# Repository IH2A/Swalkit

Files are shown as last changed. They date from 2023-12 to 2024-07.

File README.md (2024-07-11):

https://user-images.githubusercontent.com/100538879/157646195-c86fd216-0dd4-412f-9931-ac7addbbb123.mp4

> **Responsabilité  
Toute la documentation est fournie "en l'état", la chaire IH2A ne fournit aucune garantie de quelque élément que ce soit, qu'il soit explicite, implicite ou statutaire, y compris, mais sans s'y limiter, toute garantie de qualité marchande ou l’adéquation à un usage particulier ou toute garantie que le contenu des articles sera sans erreur. La chaire IH2A ne peut en aucun cas engager sa responsabilité pour tout dommage direct ou indirect, ou dommages découlant de l’utilisation de la documentation des projets partagés sur cette plateforme.**

> **Avertissement  
Les objets/projets présentés sur cette plateforme le sont UNIQUEMENT ET EXCLUSIVEMENT à titre d'informations, d'enseignements et d'exploration des possibilités du prototypage réalisable en fablab. Leur mise en avant ne constitue en aucun cas un conseil de professionnel quant à leur usage, elle ne remplace pas l'avis d'un spécialiste médical ou paramédical seul en mesure d'évaluer, de conseiller et de proposer des matériels, imprimés ou non, correspondant à une situation et des besoins précis et personnels faisant suite à la réalisation d'un bilan complet.**

> **Le Github de la chaire IH2A ([https://github.com/IH2A/](https://github.com/IH2A/)) ainsi que toutes les autres plateformes associées à la documentation de nos projets (site de communication de la chaire IH2A, [https://ih2a.insa-rennes.fr/](https://ih2a.insa-rennes.fr/)) sont le reflet de travaux de recherche appliqués aux aides technologiques au sein d'une chaire académique de recherche et de l'intérêt professionnel pour les possibilités offertes par le prototypage collaboratif en fablab.**

> **La situation de handicap est délicate et complexe et doit être évaluée et accompagnée par des professionnels.**

> **Sauf mention contraire, tous les contenus de ce projet sont sous licence [EUPL 1.2](https://eupl.eu/1.2/fr/).**
-----------------------------------------------------------------------------------------------------------------

# 1. Table des matières
- [1. Table des matières](#1-table-des-matières)
- [2. Swalkit : "Smart Walker Kit"](#2-swalkit--smart-walker-kit)
- [3. Étapes de fabrication du Swalkit](#3-étapes-de-fabrication-du-swalkit)
  - [3.1. Les outils](#31-les-outils)
  - [3.2. Le matériel](#32-le-matériel)
  - [3.3. Vue d'ensemble](#33-vue-densemble)
  - [3.4. Notice de montage](#34-notice-de-montage)
  - [3.5. Mode d'emploi du M5 stack](#35-mode-demploi-du-m5-stack)
  - [3.6. Application Android](#36-application-android)
- [4. FAQ](#4-faq)
- [5. Publications](#5-publications)
- [6. Crédits](#6-crédits)

# 2. Swalkit : "Smart Walker Kit"

Le "Swalkit" est un kit open source de "déambulateur intelligent". Il a été développé dans le cadre des travaux de recherche sur l'aide à la navigation par retour haptique pour les personnes utilisatrices de déambulateur ayant des déficiences visuelles, au sein de la [chaire académique IH2A](https://ih2a.insa-rennes.fr/) (Innovations, Handicap, Autonomie et Accessibilité) portée par l'INSA Rennes. Le dispositif "Swalkit" est reproductible : ce dépôt vise à fournir toutes les informations nécessaires afin de pouvoir explorer les possibilités du prototypage réalisables en fablab.

Le kit "Swalkit" est en effet :
- reproductible et adaptable sur des aides techniques existantes ;
- intuitif et facile à prendre en main ;
- personnalisable ; 
- à faible coût.

Le fonctionnement du kit repose sur le retour haptique fourni par les poignées du déambulateur qui informe l'usager de la position des obstacles lors de la déambulation. 
Il est composé de 3 ensembles à fixer sur l'aide technique à équiper : 
- capteurs ;
- moteurs vibrants ;
- unité de contrôle. 

Les capteurs mesurent des distances jusqu'à 80cm. Ils sont positionnés à l'avant du déambulateur, dans des boîtiers imprimés en 3D disposés de chaque côté, afin de permettre la détection d'obstacles devant le déambulateur et sur les côtés. Les moteurs vibrants sont positionnés au plus proches des poignées dans des boîtiers imprimés en 3D. L'unité de contrôle récupère les mesures de distances effectuées par les capteurs puis envoie un signal à chaque moteur pour les activer afin de signaler la présence d'un obstacle à l'usager par vibration de la poignée dans sa main.
<p align="center">walker

Une app mobile Android permet de personnaliser la configuration du comportement des moteurs. Ainsi, il est possible de définir plusieurs profils pour différents usagers et différents contexte d'usage (exemple : intérieur, extérieur, domicile, etc.).
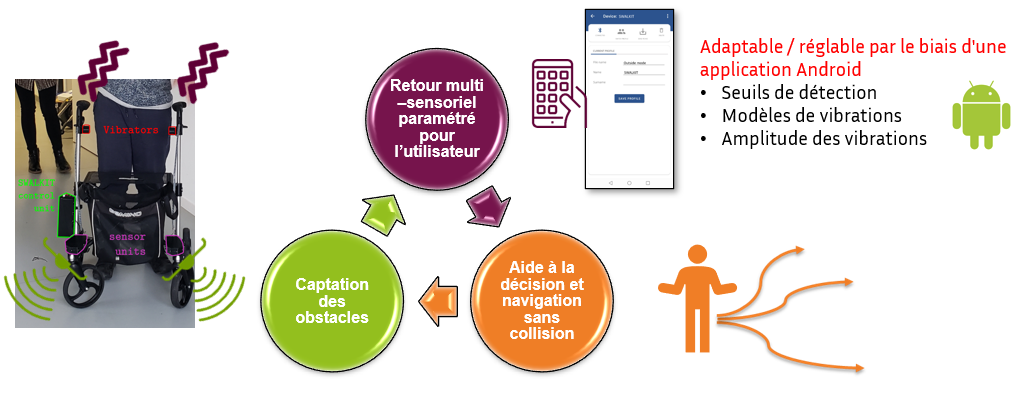
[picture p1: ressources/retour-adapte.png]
schema
<p align="center">

Le reste de la page indique comment fabriquer son kit, et les publications scientifiques dont le kit a fait l'objet.
L'ensemble des sources est disponible sur ce dépot.

> **Attention  
> La chaire IH2A ne fabrique pas de kit et ne fournit pas de kit. Seules les indications de montage et d'assemblage, ainsi qu'une liste de composants, sont indiquées dans ce dépôt.**

# 3. Étapes de fabrication du Swalkit

## 3.1. Les outils

La table suivante indique la liste des outils permettant la fabrication d'un kit :

|   Quel outil ?   |     Pour quoi faire ?                                               |    Remarques   |
|-----------|-|-|
|   Un ordinateur sous Windows    |  Téléverser le programme dans le microcontrôleur M5Stack AtomS3   |  Utiliser l'outil de téléversement fourni (cf [tutoriel](#33-vue-densemble))                                   |
|                   |    Adapter les modèles 3D                                           |  Utliliser un logiciel de modelisation 3d (Fusion360, Solidworks...)    |
|   Une imprimante 3D    |   Imprimer les boîtiers et interfaces mécaniques               |  Une imprimante petit format fera l'affaire         |
|   Un fer à souder    |   Il y a des points de soudure à faire sur une carte PCB pour assigner des adresses différentes aux bus I2C intelligents  |           |
|    |   Il faut souder des câbles sur les moteurs  |           |
|   Un petit tournevis cruciforme |   Pour ouvrir et fermer les différents boîtiers et fixer les capteurs |           |

## 3.2. Le matériel

La table suivante indique la liste du matériel à commander, nécessaire à la fabrication d'un kit :

|   Nom     |    Nom exact |  Pour quoi faire?   |    Fournisseur    |   Quantité nécéssaire    |     Aperçu     | Prix unitraire indicatif |
|-|-|-|-|-|-|-|
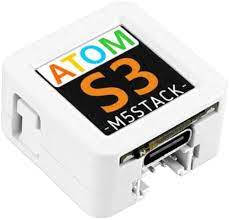
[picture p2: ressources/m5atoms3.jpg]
AtomS3
|AtomS3|M5Stack AtomS3| C'est le microcontrôleur central qui gère les capteurs, les moteurs, la logique, la communication Bluetooth...|[shop.m5stack](https://shop.m5stack.com/products/atoms3-dev-kit-w-0-85-inch-screen); [gotronic](https://www.gotronic.fr/art-module-atoms3-dev-kit-c123-37089.htm)|1|  | 17,40€|
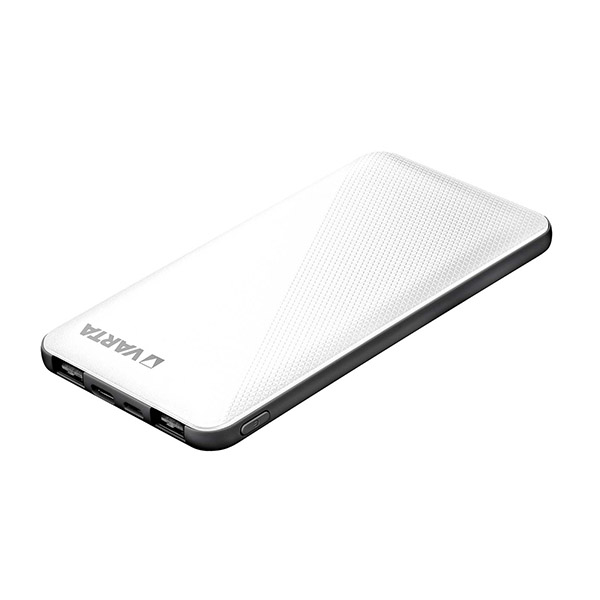
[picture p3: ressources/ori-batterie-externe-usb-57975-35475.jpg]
Batterie
|Batterie|Varta Power bank energy type 57975|C'est l'alimentation de tout le système|[gotronic](https://www.gotronic.fr/art-batterie-externe-usb-57975-35475.htm)|1| |19,90€|
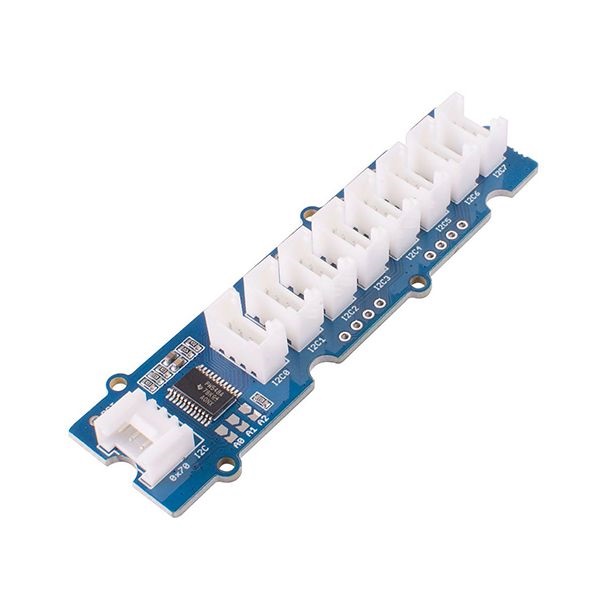
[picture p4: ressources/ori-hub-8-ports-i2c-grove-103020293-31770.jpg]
Smart Hub
|Smart Hub I2C|Grove - 8 Channel I2C Hub (TCA9548A)| Ces hubs gèrent les capteurs et permettent de les différencier sur le bus I2C|[gotronic](https://www.gotronic.fr/art-hub-8-ports-I2C-grove-103020293-31770.htm)|2| |8,05€|
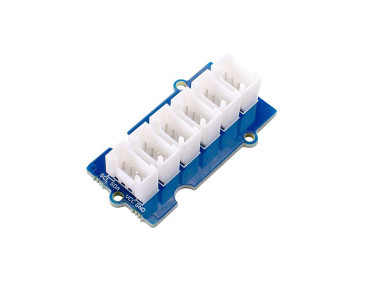
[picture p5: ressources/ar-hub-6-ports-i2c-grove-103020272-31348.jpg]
Hub I2C simple
|Hub I2C simple|Grove - I2C Hub (6 ports) v1.0|Ce hub permet de connecter l'ensemble des dispositifs sur le même bus I2C|[gotronic](https://www.gotronic.fr/art-hub-6-ports-I2C-grove-103020272-31348.htm)|1| |1,90€|
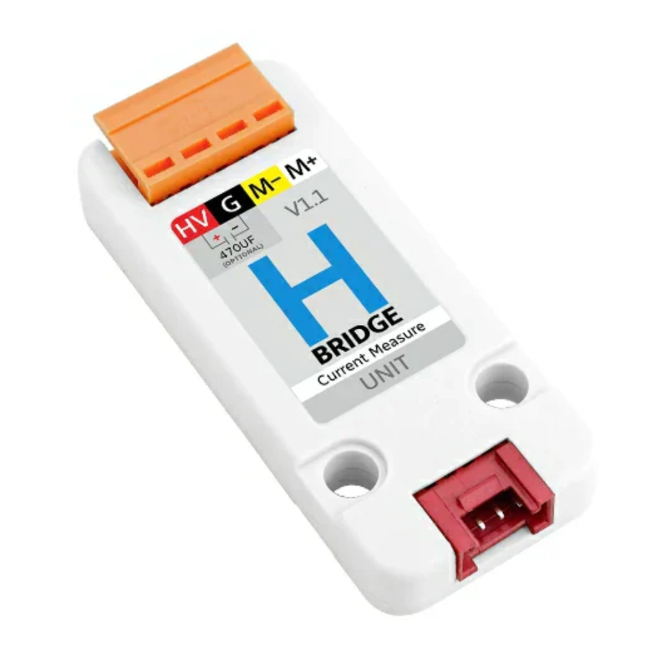
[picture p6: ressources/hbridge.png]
Pont en H
|Pont en H|Hbridge v1.1 Unit (stm32F030)|C'est un circuit électronique utilisé pour contrôler l'intensité du courant traversant un moteur|[shop.m5stack](https://shop.m5stack.com/products/h-bridge-unit-v1-1-stm32f030)|2||9€|
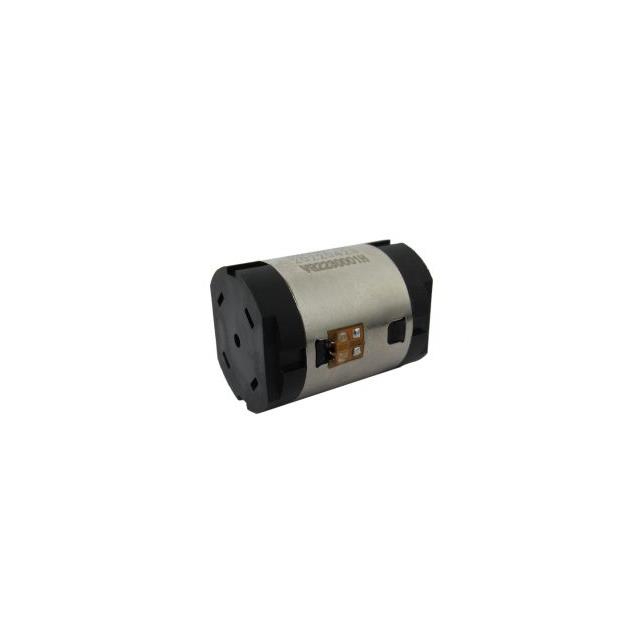
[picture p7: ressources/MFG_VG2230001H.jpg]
Moteur LMA
|Moteur LMA| - |Ce sont les moteur vibrants à positionner près des poignées du déambulateur|[digikey](https://www.digikey.fr/en/products/detail/vybronics-inc/VG2230001H/16719289)|2||7,09€|
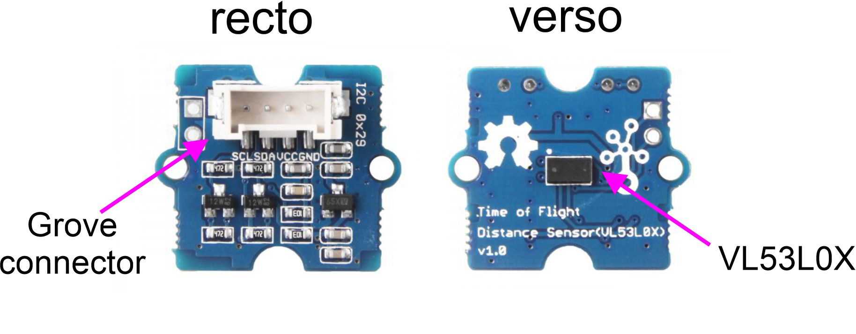
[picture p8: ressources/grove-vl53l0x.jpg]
Capteurs
|Capteurs TOF| Grove - Time of Flight Distance Sensor (VL53L0X) | Capteur "Time of flight" VL53L0X permettant la détection d'un objet dans une plage de 3 à 100 cm|[gotronic](https://www.gotronic.fr/art-module-grove-time-of-flight-101020532-28252.htm#complte_desc)|8||15,65€|
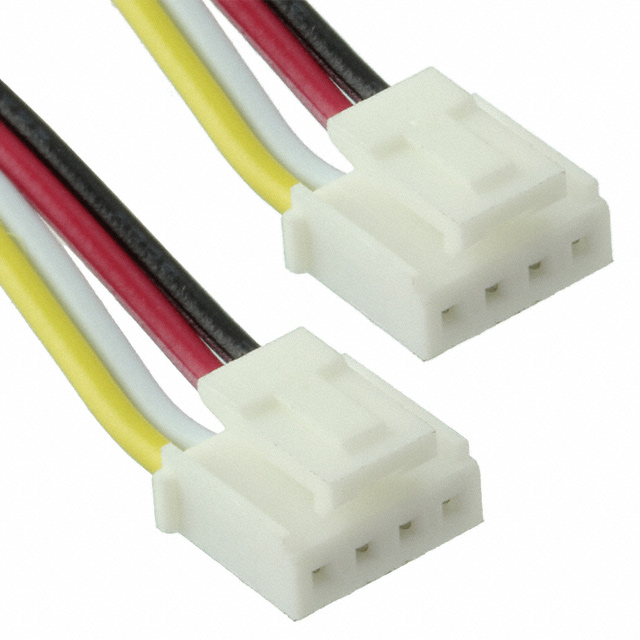
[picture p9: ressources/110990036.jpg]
grove court
|Câble grove 5cm| - |Câbles courts pour connecter les composants sur le bus I2C|[digikey](https://www.digikey.fr/en/products/detail/seeed-technology-co-ltd/110990036/5482563)|3 lots de 5||1,91€|
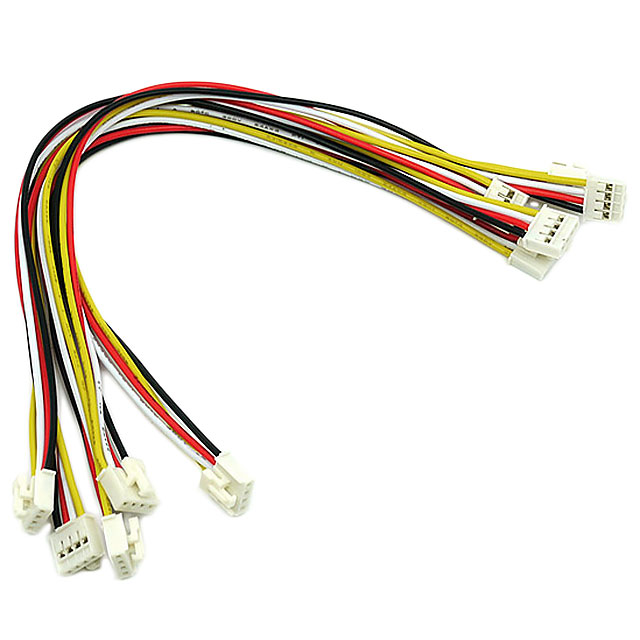
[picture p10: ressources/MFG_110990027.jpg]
grove long
|Câble grove 30cm| - |Câbles longs pour connecter les composants sur le bus I2C|[digikey](https://www.digikey.fr/en/products/detail/seeed-technology-co-ltd/110990040/5482564)|1 lot de 5||2,92€|
|Câble grove 100cm| - |Câbles très longs pour connecter les composants sur le bus I2C|[mouser](https://www.mouser.fr/ProductDetail/M5Stack/A034-D?qs=81r%252BiQLm7BQIX3ZPS9TpAA%3D%3D)|1 lot de 5|grove long|1,81€|
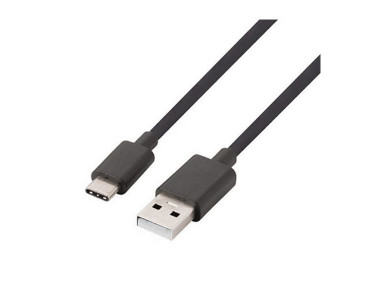
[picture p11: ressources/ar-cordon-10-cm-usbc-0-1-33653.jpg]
USBC
|Câble USB-C| - |Pour téléverser le programme, alimenter l'atomS3 et recharger la batterie|[gotronic](https://www.gotronic.fr/art-cordon-10-cm-usbc-0-1-33653.htm)|1||4,30€|
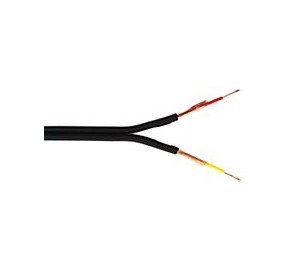
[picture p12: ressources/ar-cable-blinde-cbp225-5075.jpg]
câble
|Câble d'alimentation moteur| - |Pour alimenter les moteurs vibrants|à titre indicatif: [gotronic](https://www.gotronic.fr/art-câble-blinde-cbp225-5075.htm)|2 mètres||~1€/m|
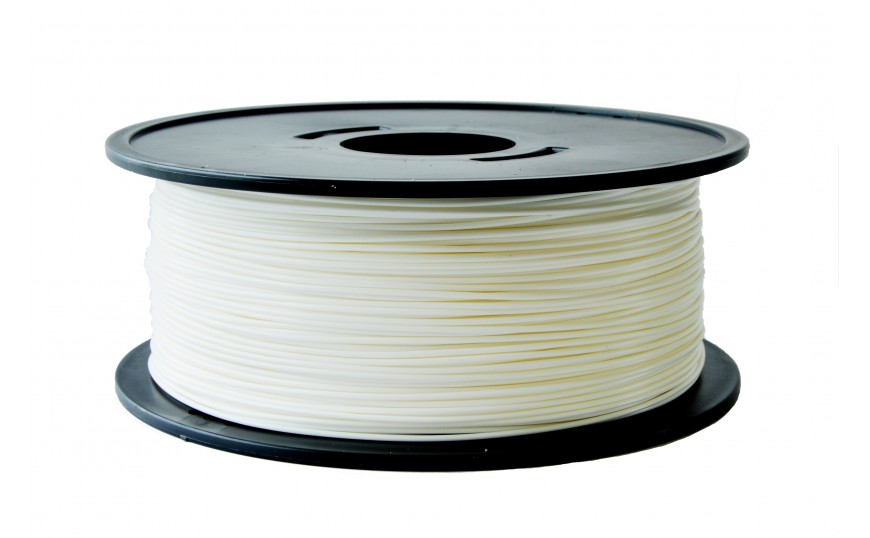
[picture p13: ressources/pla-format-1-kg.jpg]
PLA
|Bobine PLA| - |Pour imprimer les boîtiers|à titre indicatif : [arianeplast](https://www.arianeplast.com/3d-filament-recycle/195-pla-recycle-couleur-metallise-filament-175mm.html)|<1kg||~20€/kg|
|Visserie| - |Pour l'assemblage|[M3x8mm = 6</br>M3x15mm = 14</br>Écrous M3 = 20</br>M2x8mm = 25</br>Écrous M2 = 16](https://www.bricovis.fr/produit-vis-a-tete-fraisee-hexagonale-creuse-filetage-total-inox-a2-din-7991-tfhca2/)|-||
|Gaine spirale| - |Pour organiser les câbles|[leroy merlin](https://www.leroymerlin.fr/produits/electricite-domotique/rallonge-multiprise-enrouleur-et-cable-electrique/gaine-electrique-icta/gaine-spirale-p.html)|2 mètres||
|Scotch| - |Pour coller les moteurs||-||
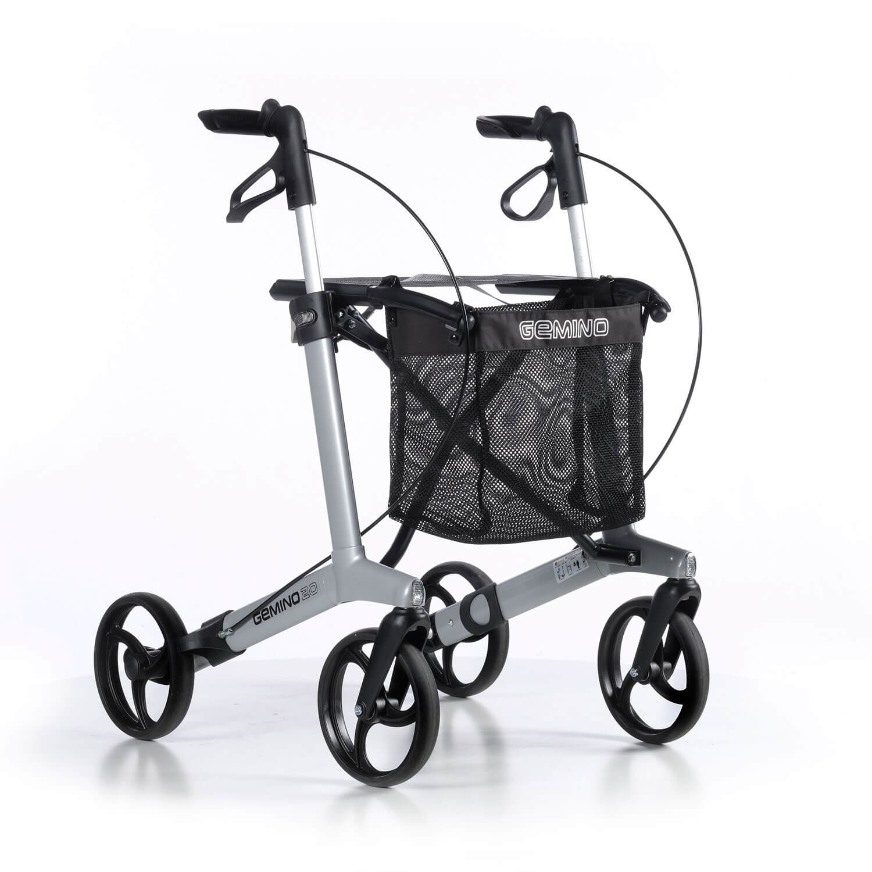
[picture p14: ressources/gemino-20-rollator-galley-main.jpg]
rollator
|Déambulateur| - |Le gemino est utilisé comme base||1||615€|

## 3.3. Vue d'ensemble

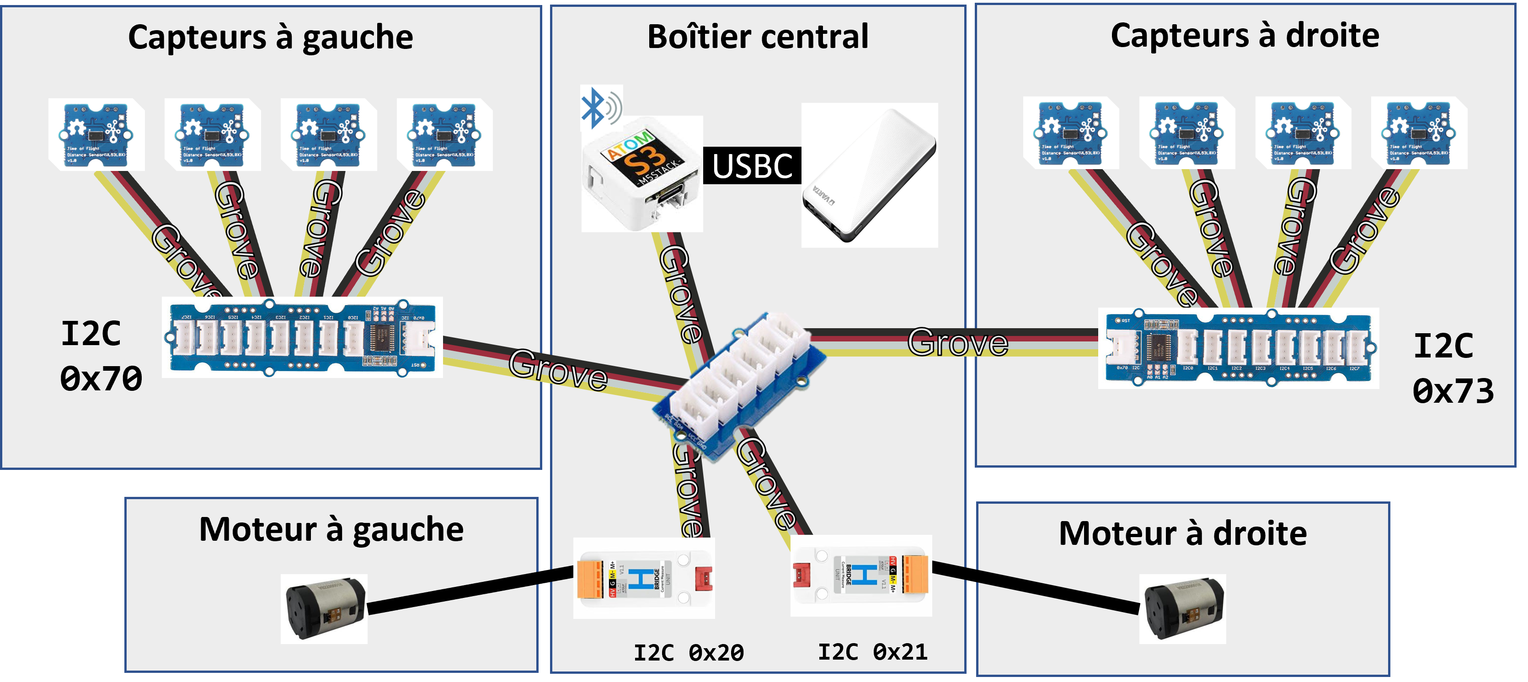
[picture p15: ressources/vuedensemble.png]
vuedensemble


## 3.4. Notice de montage

> Note de première mise en route : Lorsque le programme est téléversé le M5stack démarre. Celui-ci commence à communiquer avec les différents modules. Les ponts en H ont besoin d'être mis à jour pour contrôler correctement les moteurs. En effet, ces moteurs ont besoin d'une alimentation qui alterne son sens à 70Hz pour fonctionner correctement. Or, le programme de ces ponts en H alterne le sens du courant à la demande. **Nous mettons à jour ce programme automatiquement via le M5Stack et la communication I2C** pour que l'alternance de sens soit gérée directement dans le pont en H.

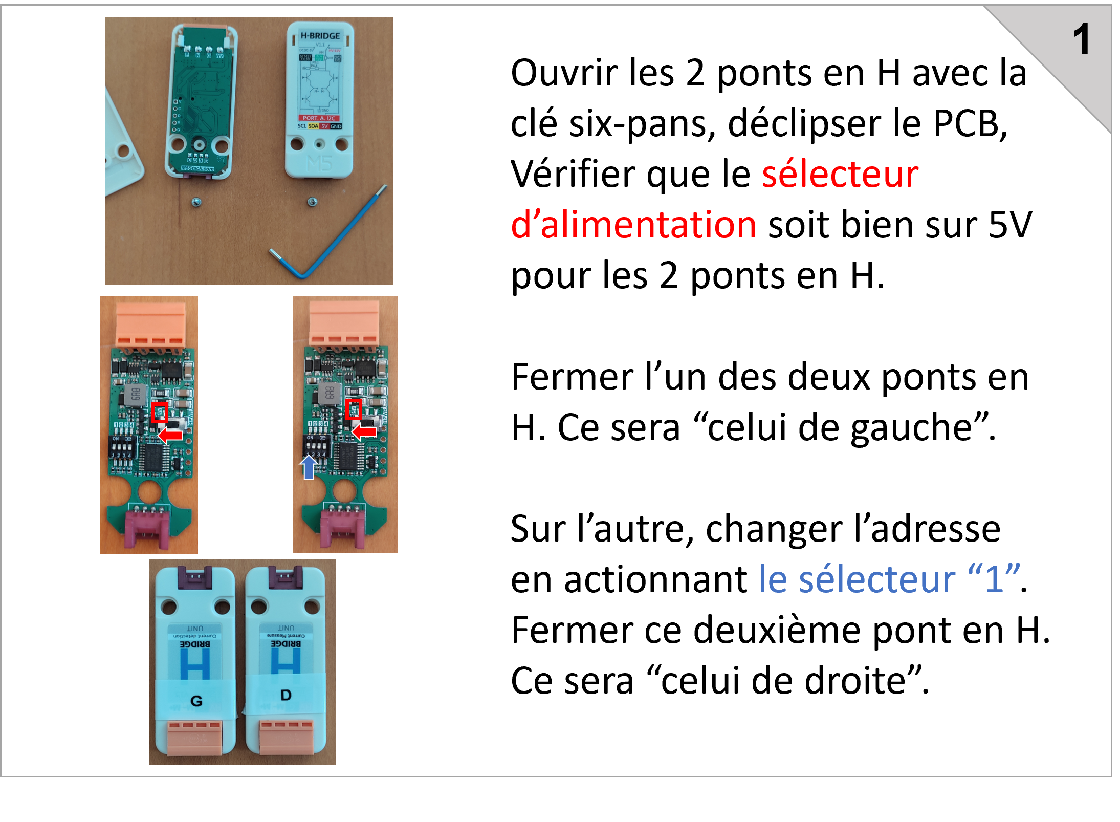
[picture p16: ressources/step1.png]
step1

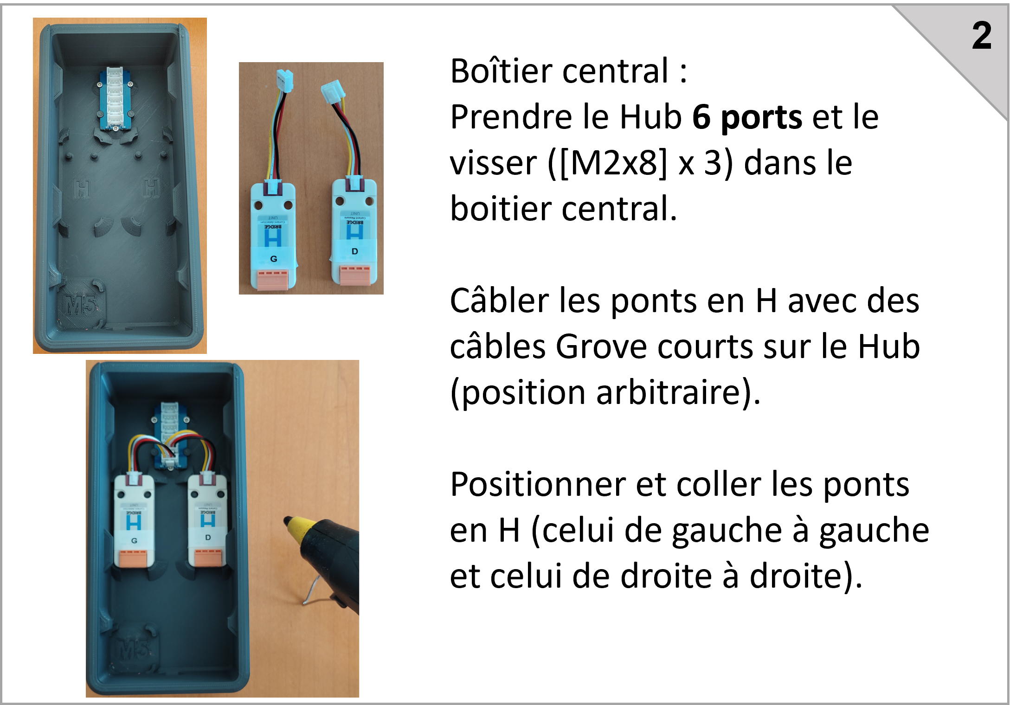
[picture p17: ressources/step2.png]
step2

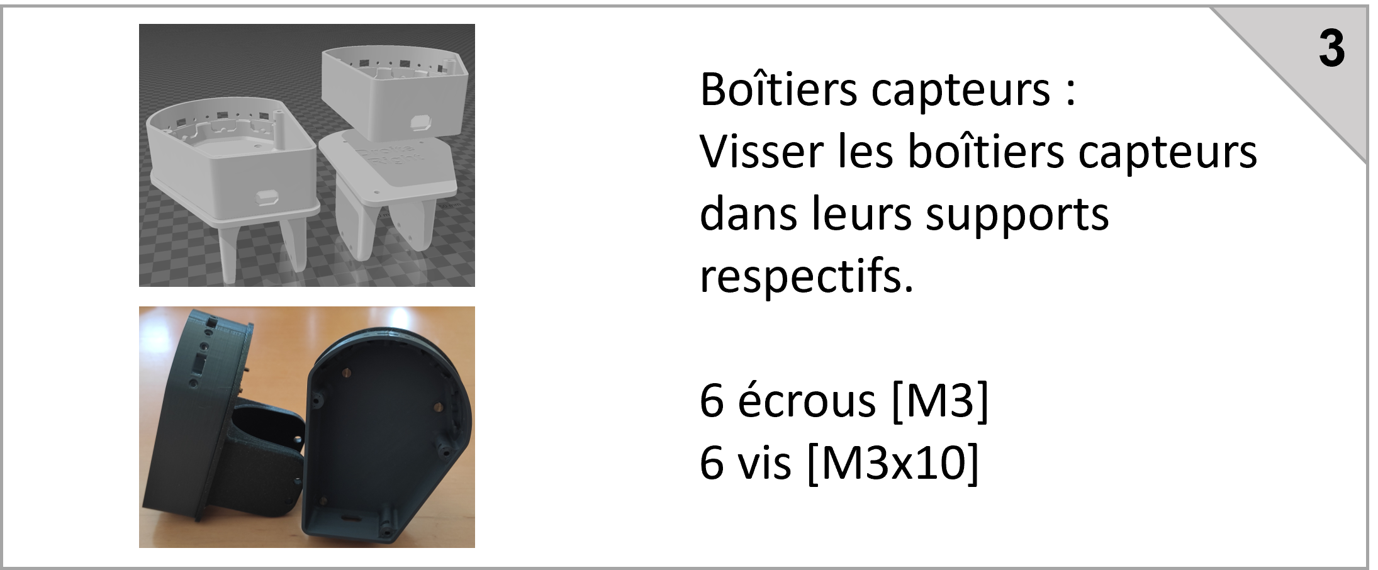
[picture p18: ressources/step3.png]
step3

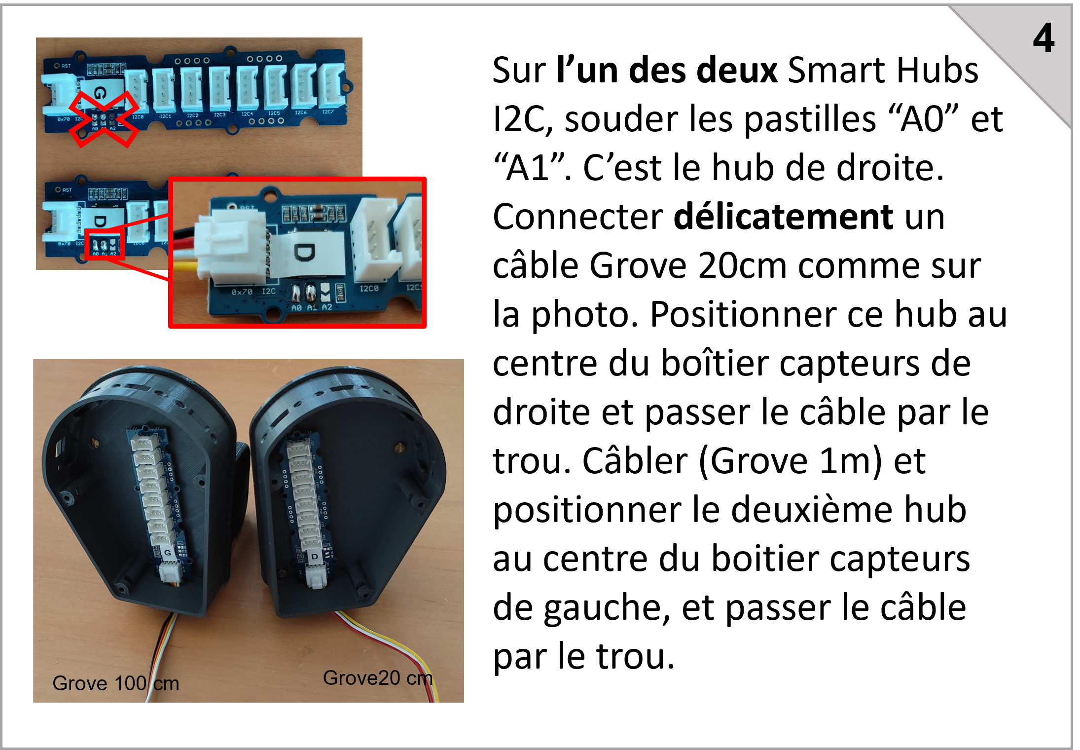
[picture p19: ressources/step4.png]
step4

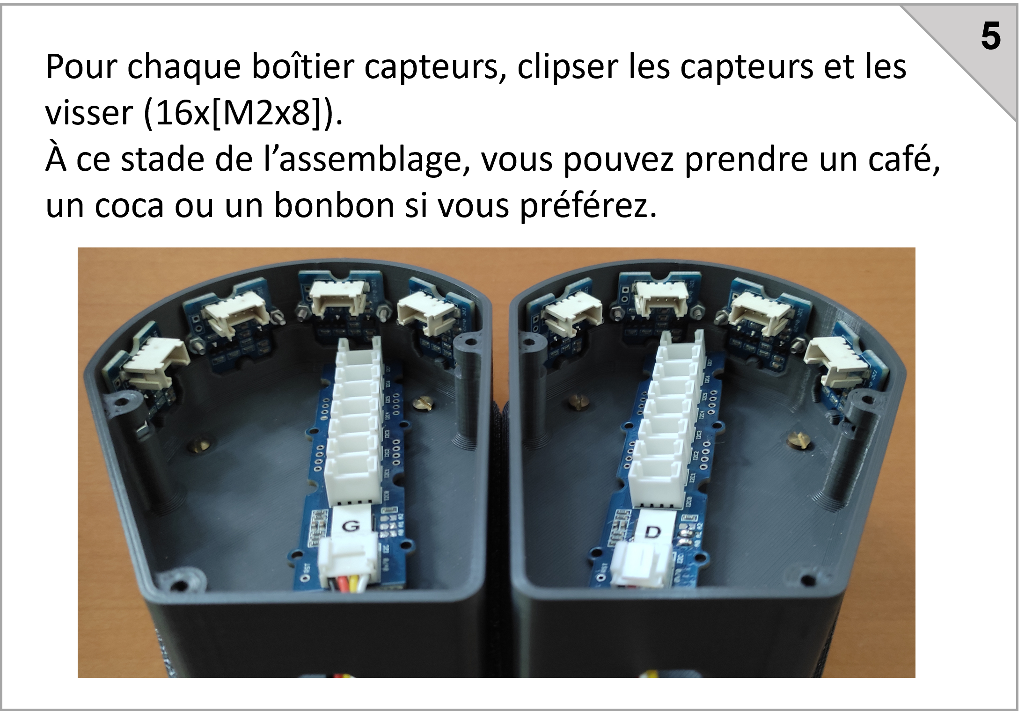
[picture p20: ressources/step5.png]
step5

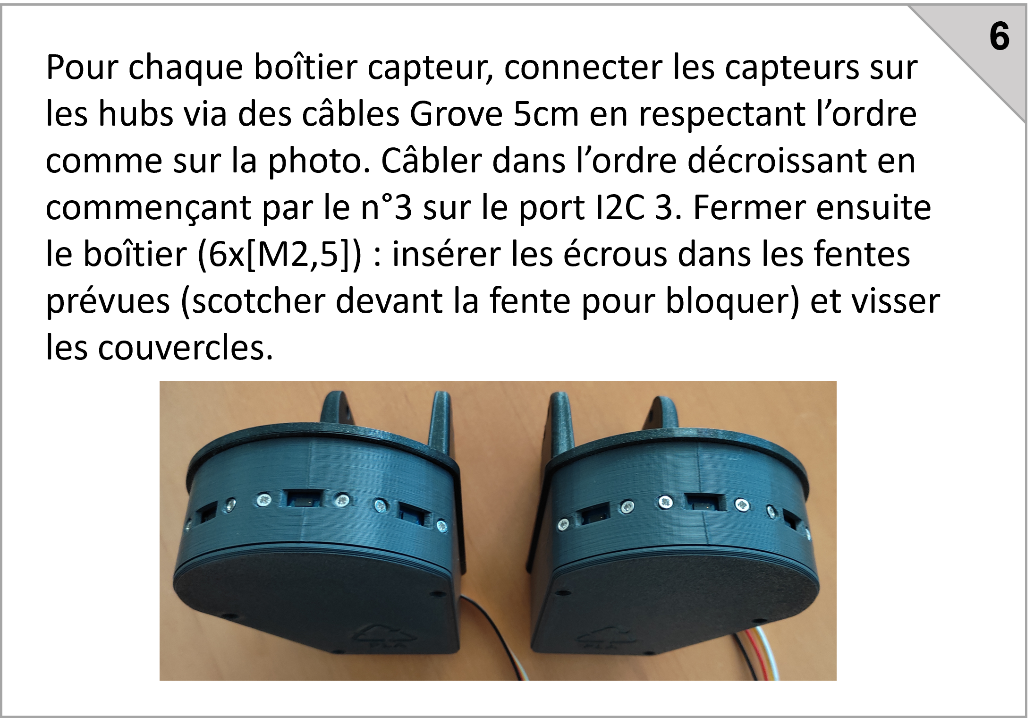
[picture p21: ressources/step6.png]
step6

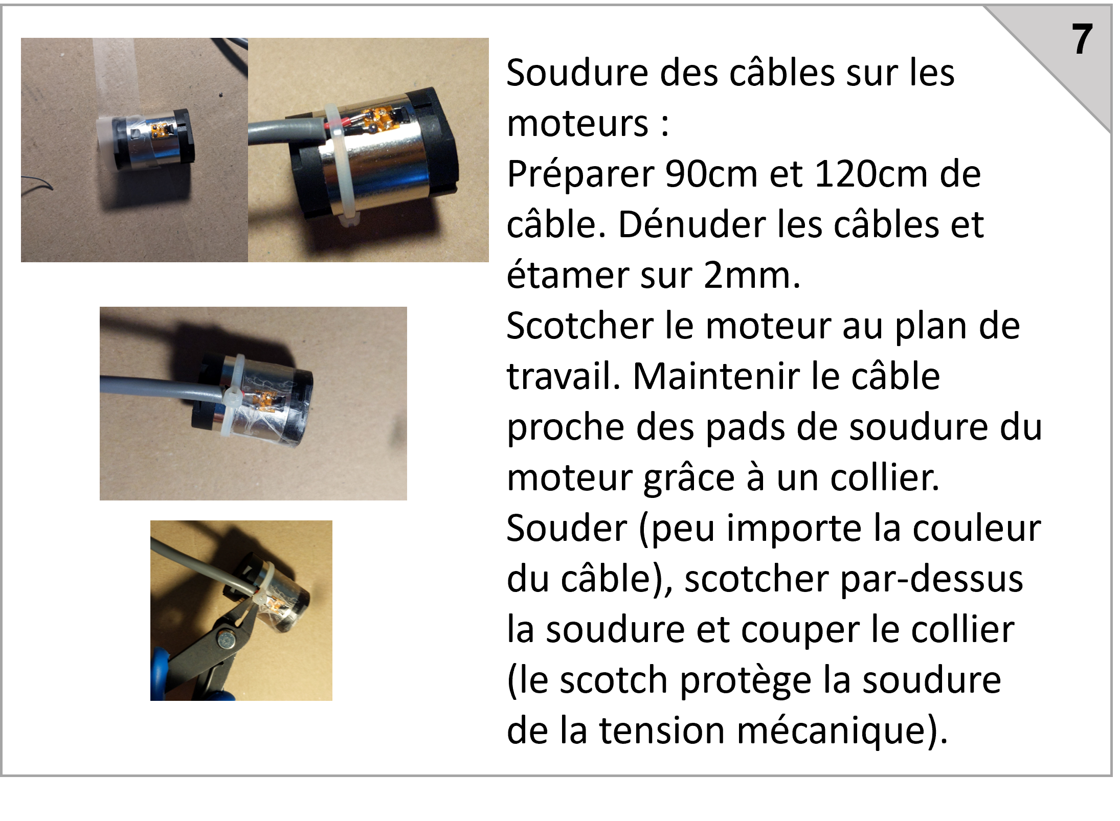
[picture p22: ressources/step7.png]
step7

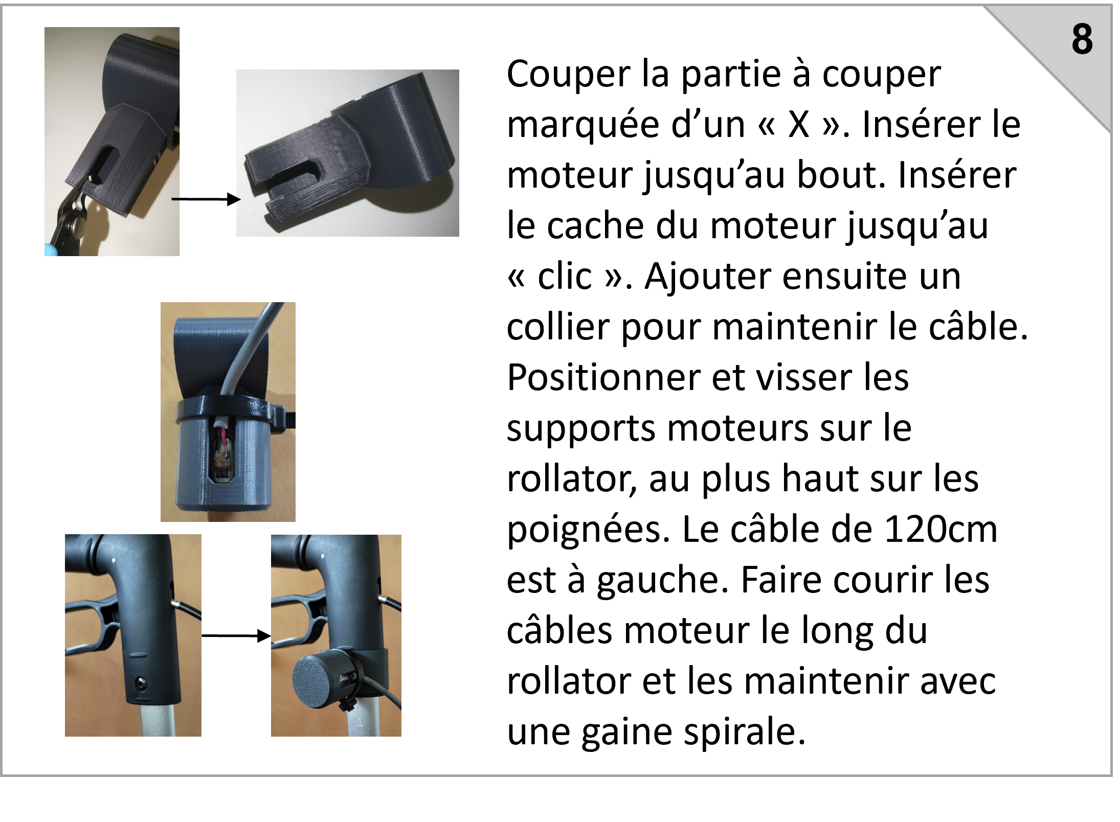
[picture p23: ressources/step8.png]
step8

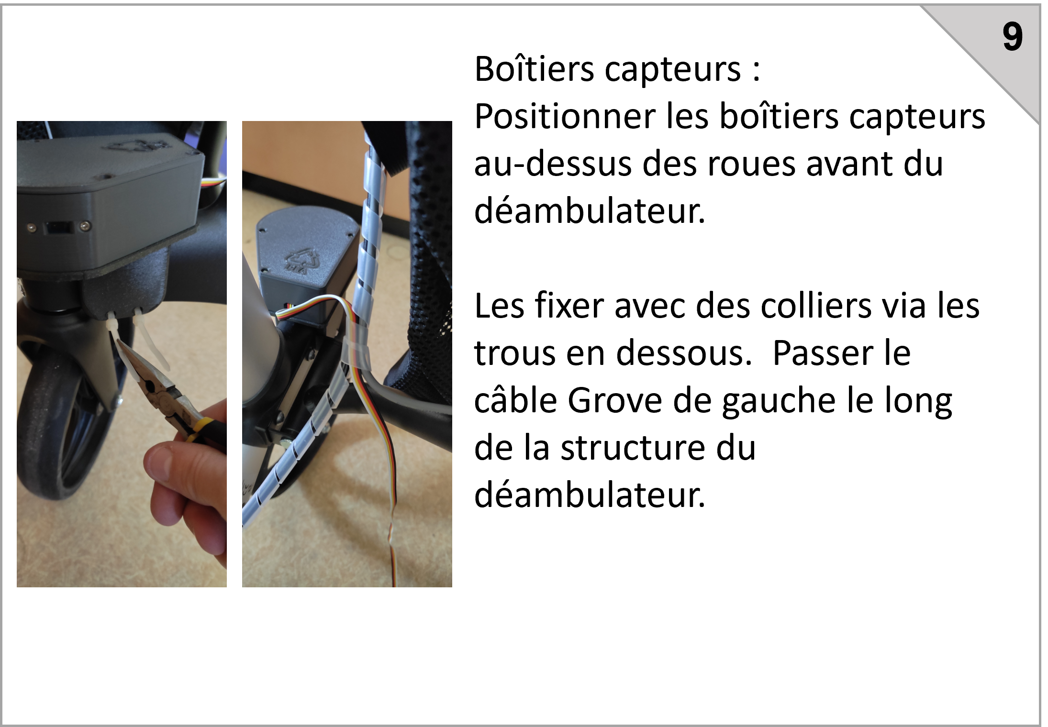
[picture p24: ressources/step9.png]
step9

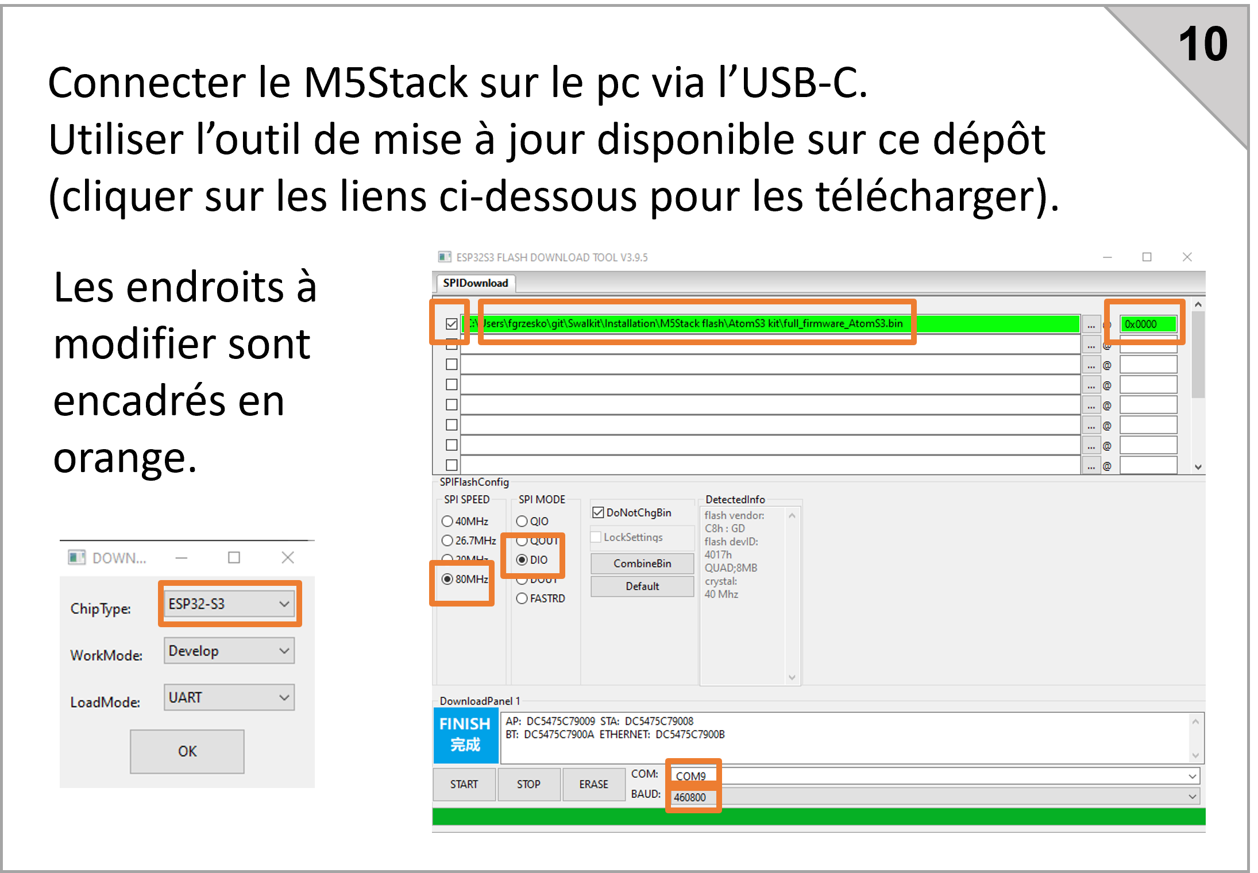
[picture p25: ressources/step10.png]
step10


<a href="../../raw/master/Installation/M5Stack%20flash/flash_download_tool_3.9.5.exe" target="_blank">Outil de mise à jour</a><br/>
<a href="../../raw/master/Installation/M5Stack%20flash/full_firmware_AtomS3.bin" target="_blank">Microcode</a><br/>

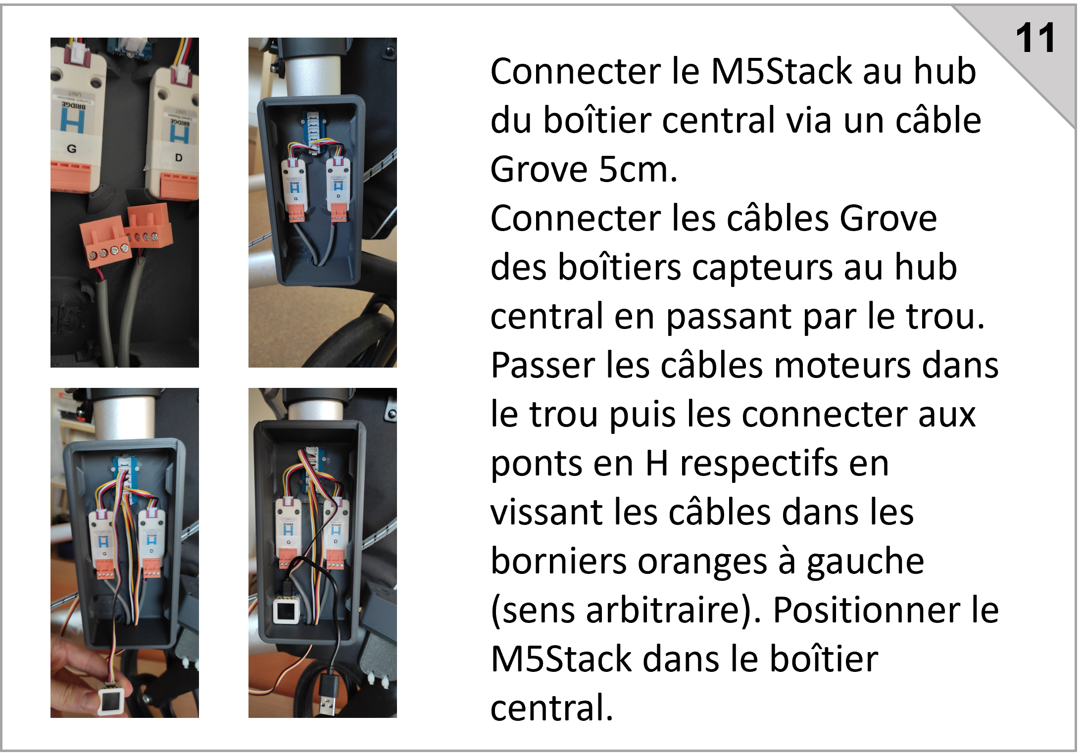
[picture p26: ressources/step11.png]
step11

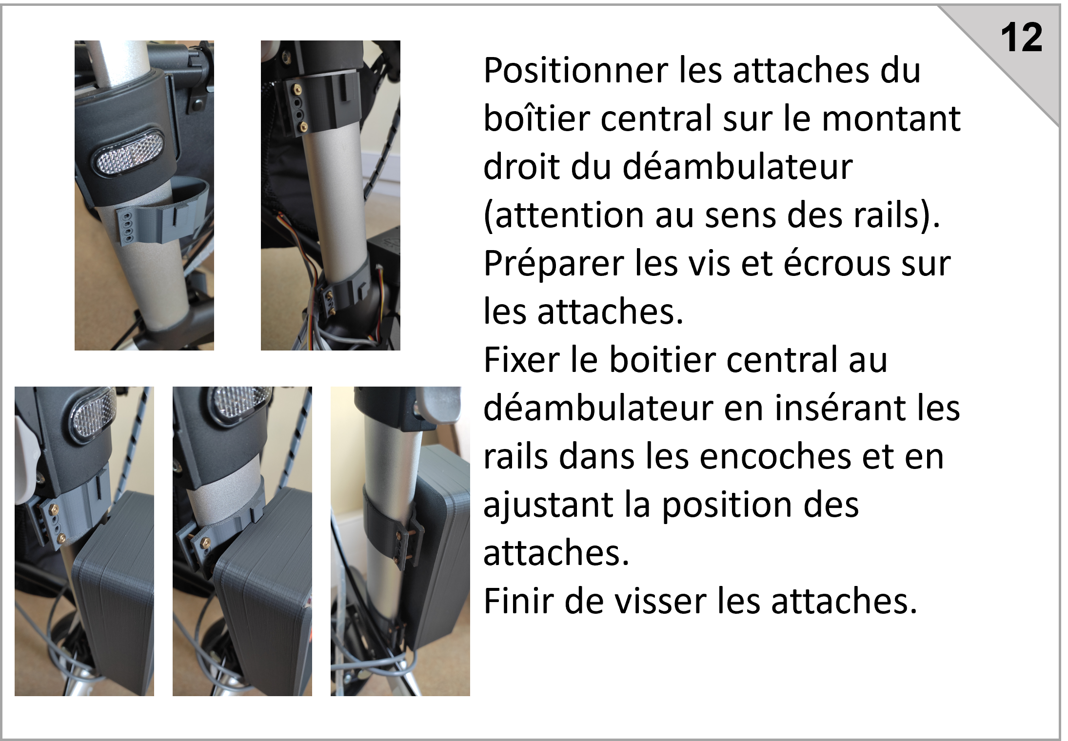
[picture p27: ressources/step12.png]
step12

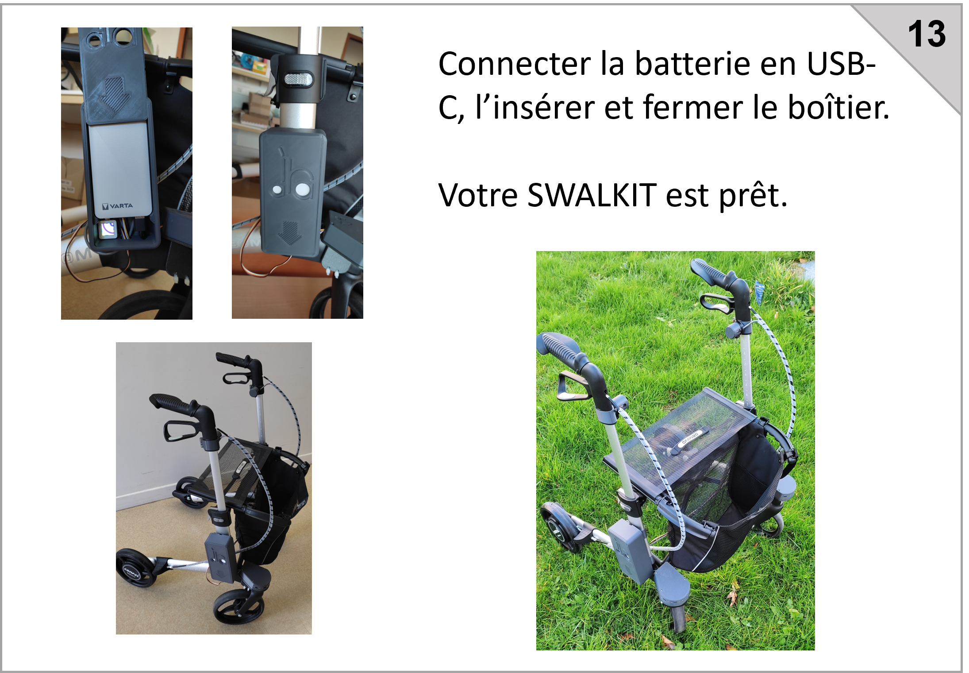
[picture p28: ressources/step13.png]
step13


## 3.5. Mode d'emploi du M5 stack

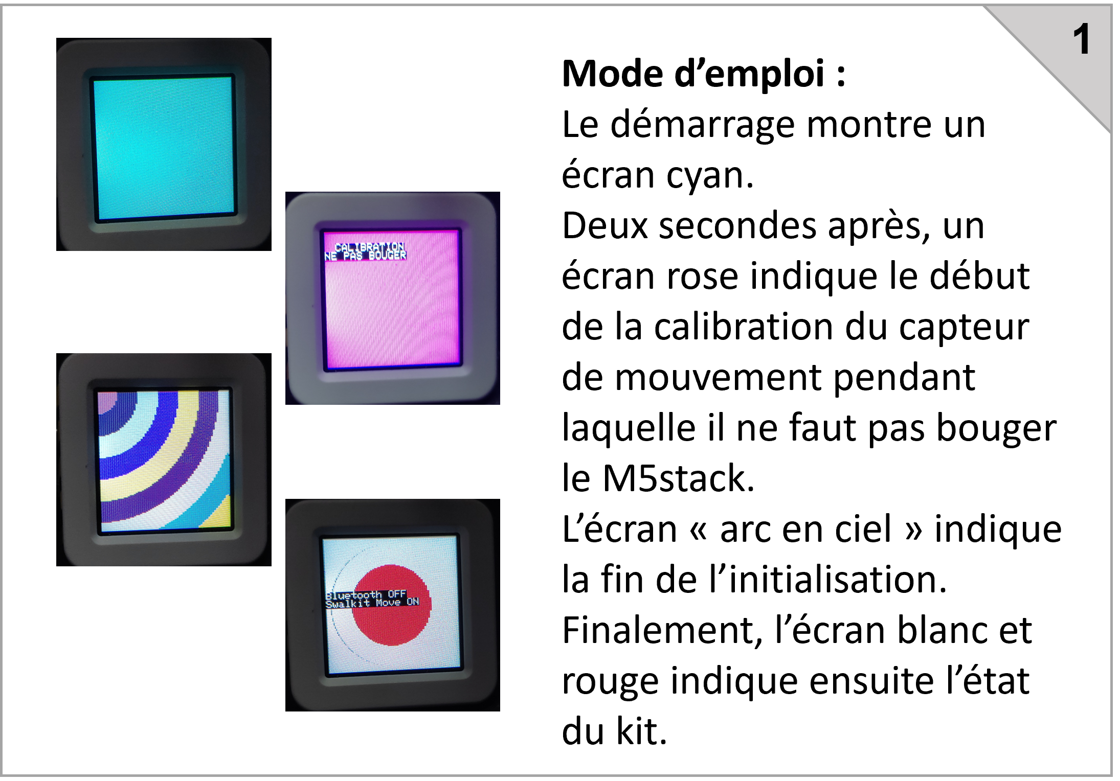
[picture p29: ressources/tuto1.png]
tuto1

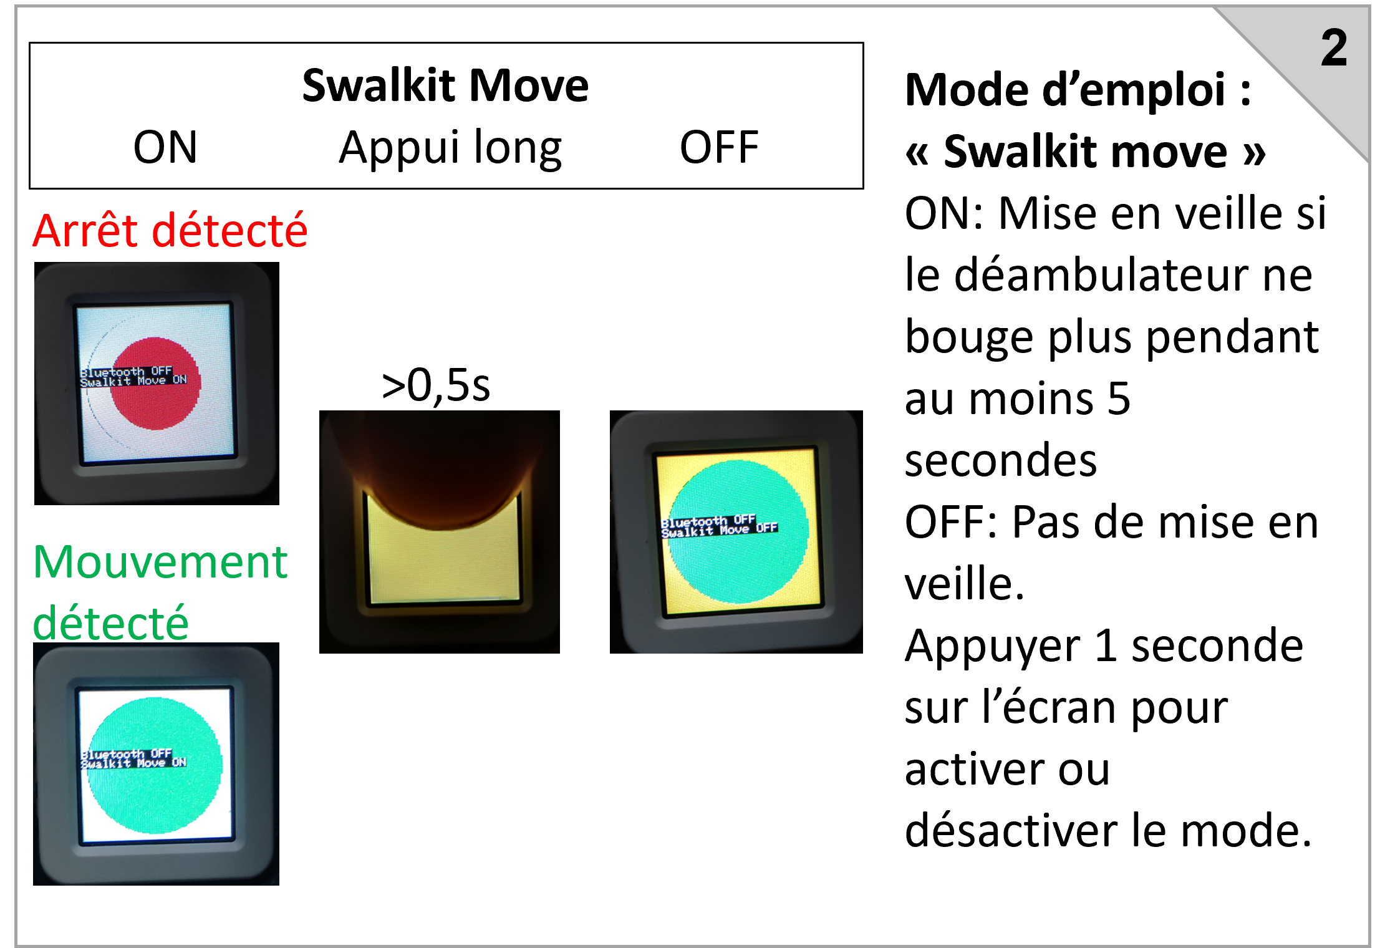
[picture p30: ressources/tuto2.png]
tuto2

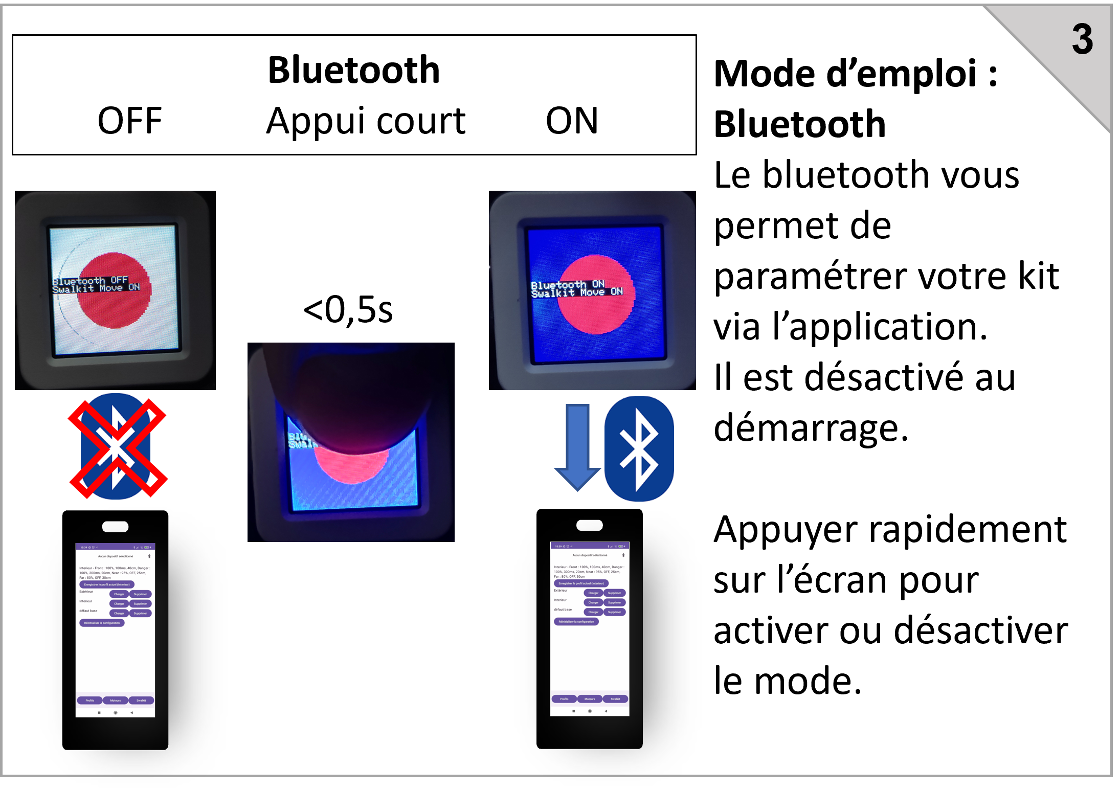
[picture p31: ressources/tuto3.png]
tuto3


## 3.6. Application Android

L'application Android permet de :
- Définir des profils
- Sélectionner un profil pour le modifier, ou l'envoyer au kit
- Lire les données des capteurs
  
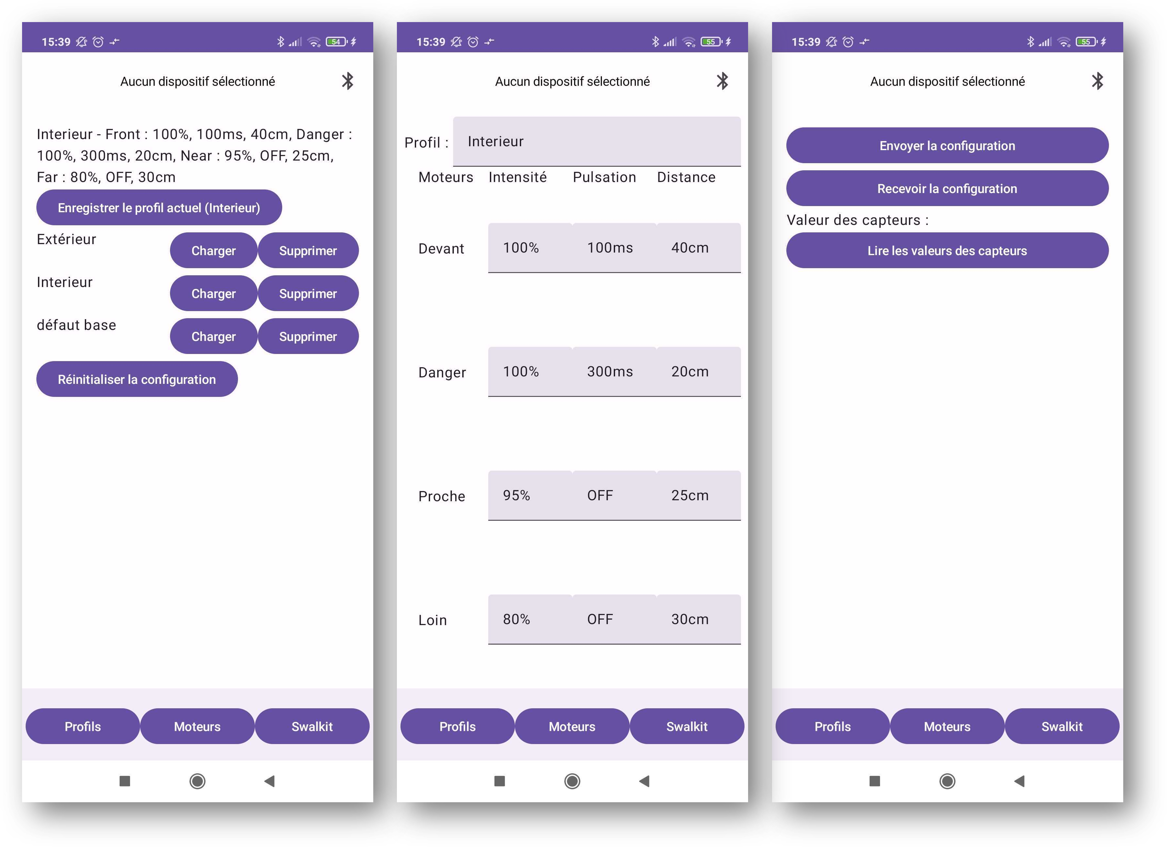
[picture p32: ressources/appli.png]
smarthub boîtiers montés


Le Bluetooth du kit est désactivé au démarrage. Il faut appuyer sur l'écran du M5Stack AtomS3 (qui est en fait un bouton). L'écran de l'AtomS3 devient alors bleu. Vous pouvez alors appairer votre téléphone avec le kit dans vos paramètres Bluetooth.

Une fois que celà est fait vous pouvez télécharger le [fichier d'installation (.apk) de l'application](https://github.com/IH2A/Swalkit/raw/master/Installation/App/app-release.apk).
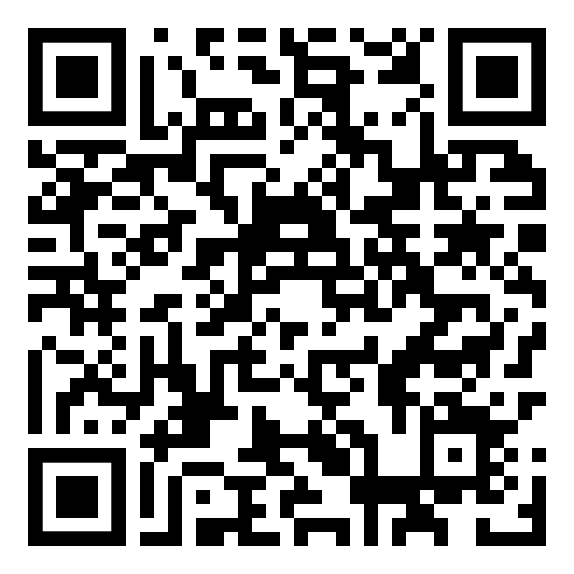
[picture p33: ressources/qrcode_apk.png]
qrcode QRCode du lien vers le fichier apk


Une fois l'installation faite, vous pouvez vous connecter au kit en sélectionnant l'icône Bluetooth de l'application. L'application requiert la permission d'utiliser le Bluetooth ainsi que d'accèder à la localisation du téléphone pour pouvoir communiquer avec le M5Stack, ces autorisations doivent être accordées lorsque le téléphone le demande.

La première page permet de gérer les profils, les sélectionner, les enregistrer, les réinitialiser.

La deuxième page permet de modifier le profil sélectionné. Une fois modifié, il faut penser à l'enregistrer sur la première page.

La dernière page permet d'envoyer le profil courant au kit, de recevoir la configuration courante du kit, ou de lire les valeurs des capteurs au moment où on appuie sur le bouton associé à la lecture des capteurs.

Il peut être judicieux d'appuyer sur l'écran de l'AtomS3 pour désactiver la communication Bluetooth une fois la configuration faite, bien que celle-ci soit peu gourmande en energie (BLE). L'AtomS3 garde la dernière configuration en mémoire lorsque celui ci s'éteint.

# 4. FAQ
>**J'aimerais me procurer un SWALKIT, comment faire ?**
>
>Le plus simple est de se rapprocher d'un fablab local. Nous fournissons simplement la notice mais ne pouvons faire plus.

>**Mon SWALKIT ne vibre plus après quelques secondes à l'arrêt**
>
>Le SWALKIT ne fait pas vibrer les moteurs lorsque le déambulateur n'a pas bougé depuis plusieurs secondes. Cette option peut être désactivée via un appui long sur l'écran du M5stack.

>**Mon SWALKIT a un comportement étrange**
>
>S'il s'agit d'une première mise en route, vérifiez l'ensemble du câblage. Assurez vous d'avoir donné la bonne addresse à chaque dispositif I2C, une inversion est vite arrivée.
>
>Si ce n'est pas une première utilisation : vérifiez d'abord que vos capteurs fonctionnent. Pour cela utilisez l'application en activant le bluetooth du kit via un appui court sur l'écran du M5stack. Mettez-vous dans un environnement dégagé et appuyez sur le bouton de lecture des capteurs : chaque capteur doit envoyer une valeur entre 70 et 80 (cm). Mettez votre doigt devant un capteur sans occulter les autres, et réappuyez sur le bouton : un des capteurs doit envoyer une valeur faible de l'ordre de quelques cm. La plage de detection des capteur est de 3 cm à 8 cm.
>
>Par ailleurs, le m5AtomS3 peut être perturbé par un bus I2C instable : **n'hésitez pas à le redémarrer en débranchant et rebranchant l'USB-C.**

>**Je ne parviens pas à me connecter au SWALKIT via l'application Android**
>
>Assurez-vous que l'application dispose bien des autorisations pour utiliser le Bluetooth, ainsi que pour accèder à la position du téléphone (la position - ou localisation - n'est pas utilisée en tant que telle mais cette autorisation est nécessaire pour permettre l'établissement de la communication Bluetooth Low Energy entre le téléphone et le M5Stack).
>Pour ce faire, vous pouvez vérifier dans les paramètres des applications du téléphone, sections autorisations, qu'aucune autorisation n'est indiquée comme bloquée, ou refusée, et les autoriser le cas échéant.
>Assurez-vous aussi que la localisation est activée ("Localisation" ou "Position" suivant les téléphones)

# 5. Publications

Citer : [GRZESKOWIAK, Fabien, DEVIGNE, Louise, PASTEAU, François, et al. SWALKIT: A generic augmented walker kit to provide haptic feedback navigation assistance to people with both visual and motor impairments. In : 2022 International Conference on Rehabilitation Robotics (ICORR). IEEE, 2022. p. 1-6.](https://hal.science/hal-03709659/document)

Présentation au congrès SOFMER 2022.

# 6. Crédits

Co-financé par [Inria - Défi DORNELL](https://project.inria.fr/dornell/) et [Sopra Steria Mission Handicap](https://www.missionhandicap.soprasteria.com/).

Auteurs principaux : Fabien GRZESKOWIAK et Thomas VOISIN.

Le swalkit a été développé par [la chaire IH2A.](https://ih2a.insa-rennes.fr/)
(https://ih2a.insa-rennes.fr/)

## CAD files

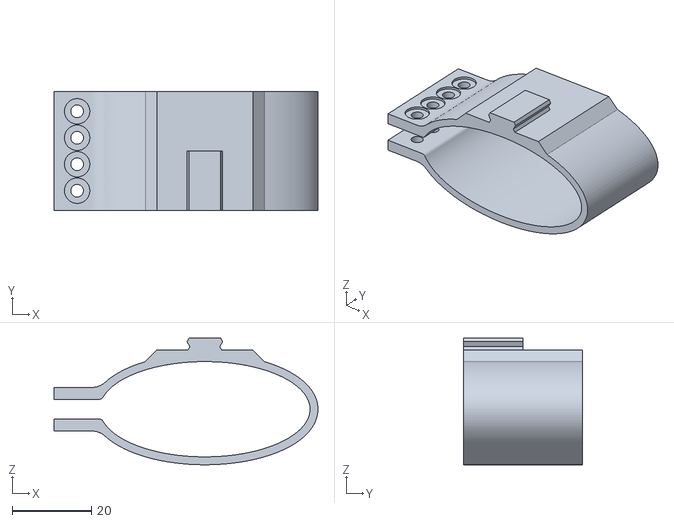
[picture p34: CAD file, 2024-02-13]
Installation/3D print/FixationChassis.2024.02.12.001.stl
66.5 x 30.0 x 31.9

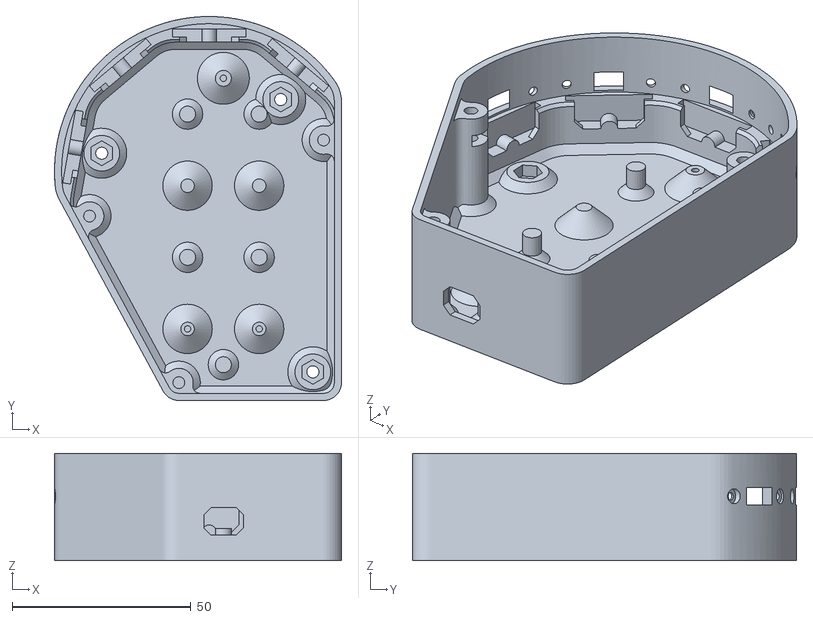
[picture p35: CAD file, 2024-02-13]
Installation/3D print/BoîtierCapteurs_Gauche.2024.02.12.001.stl
80.2 x 107.3 x 30.0

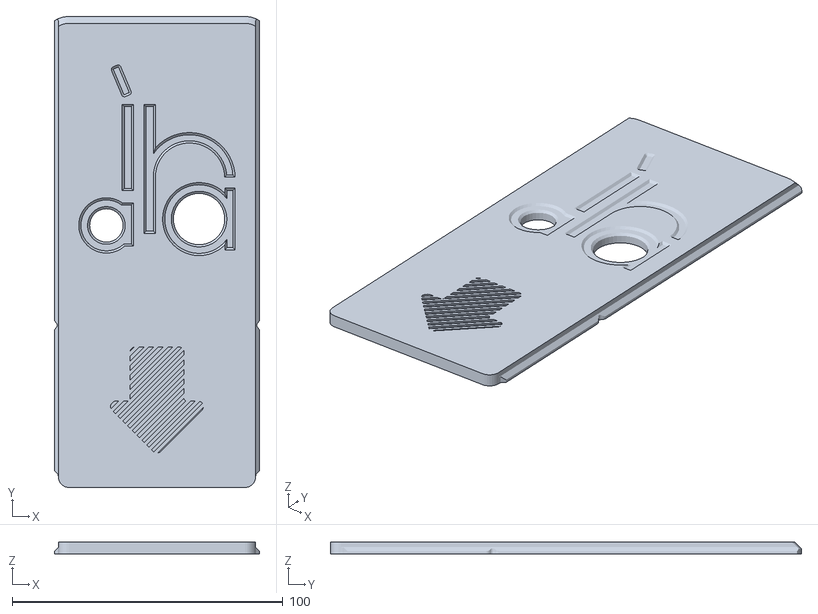
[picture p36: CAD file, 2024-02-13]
Installation/3D print/CouvercleBoitierElec.2024.02.12.001.stl
75.8 x 173.9 x 4.41

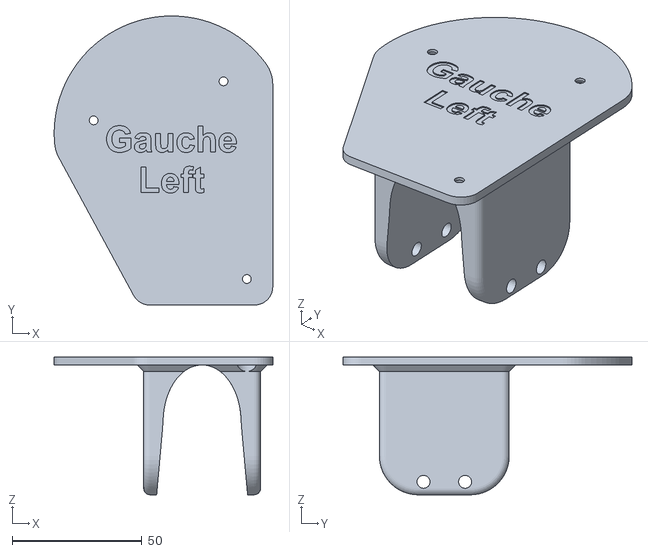
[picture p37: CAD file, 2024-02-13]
Installation/3D print/SupportBoîtierCapteurs_Gauche.2024.02.12.001.stl
84.2 x 111.3 x 53.0

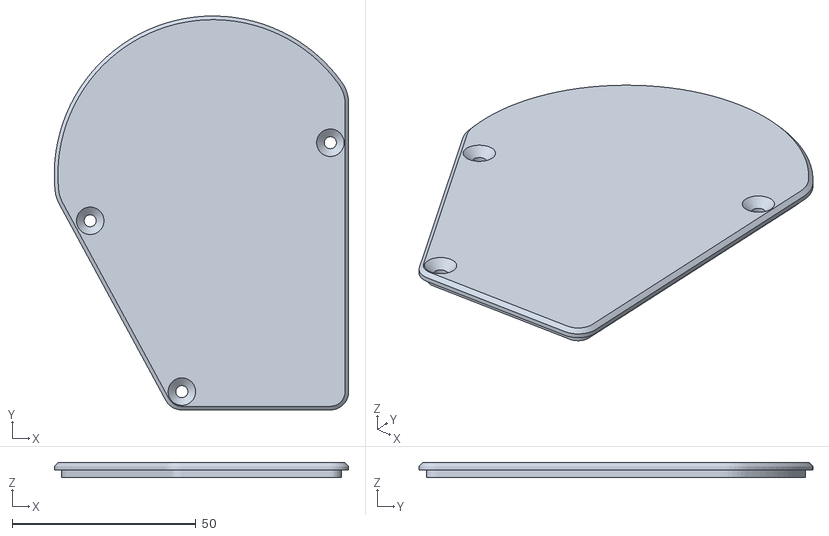
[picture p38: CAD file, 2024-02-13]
Installation/3D print/CouvercleBoîtierCapteurs_Gauche.2024.02.12.001.stl
80.2 x 107.3 x 4.00

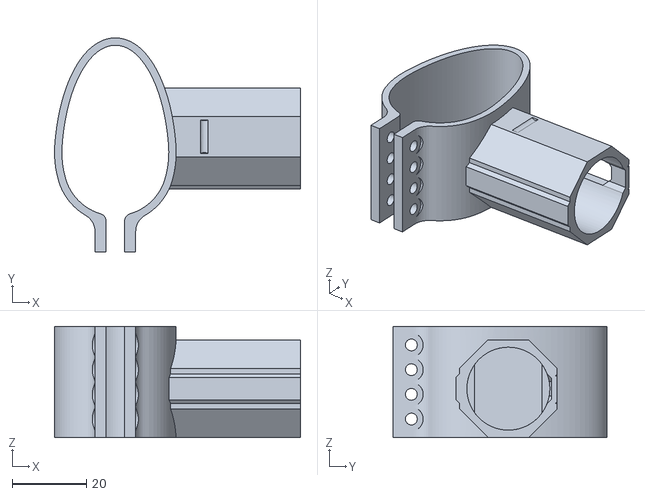
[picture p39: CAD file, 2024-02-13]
Installation/3D print/BlocMoteur(sans_supports).2024.02.12.001.stl
66.4 x 57.9 x 30.0

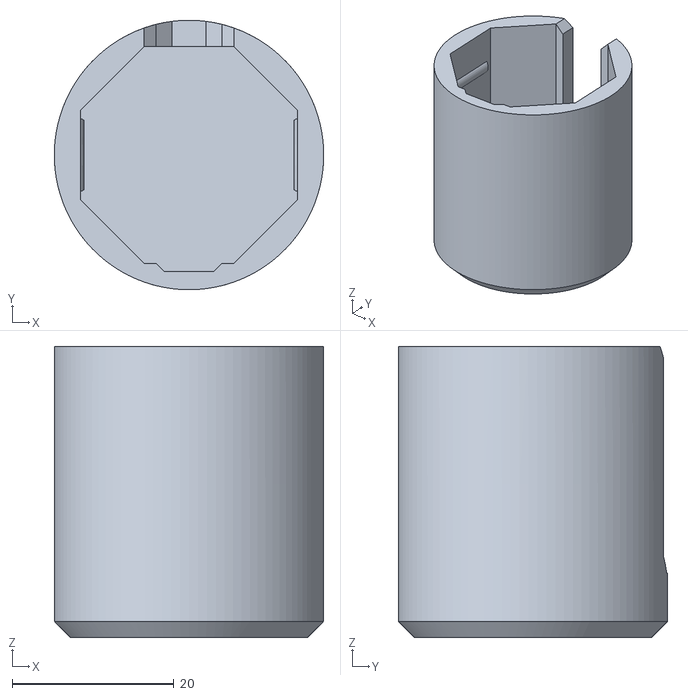
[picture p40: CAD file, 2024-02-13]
Installation/3D print/CapotMoteur.2024.02.12.001.stl
33.3 x 33.3 x 36.0

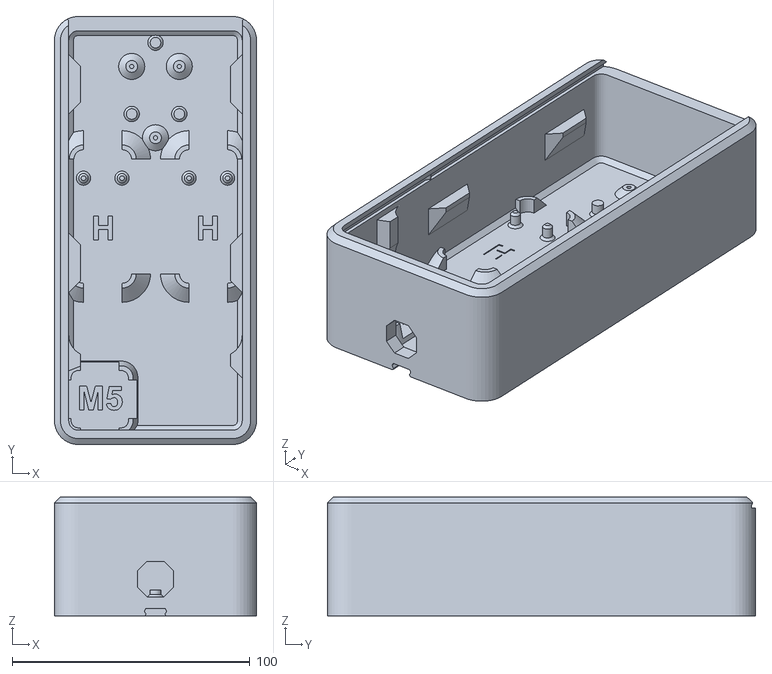
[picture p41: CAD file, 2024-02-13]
Installation/3D print/BoitierElec.2024.02.12.001.stl
85.0 x 180.0 x 50.0

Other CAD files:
Installation/3D print/BoîtierCapteurs_Droite.2024.02.12.001.stl
Installation/3D print/CapotMoteur(mirroir).2024.02.12.001.stl
Installation/3D print/FixationChâssis(miroir).2024.02.12.001.stl
Installation/3D print/SupportBoîtierCapteurs_Droite.2024.02.12.001.stl
Installation/3D print/CouvercleBoîtierCapteurs_Droite.2024.02.12.001.stl
Installation/3D print/BlocMoteur(sans_supports)(miroir).2024.02.12.001.stl
Developpement/3D files/central unit/Final - Boîte Élec 2023 v23.f3d
Developpement/3D files/motor cases/Final - Motor Case Clean Swalkit v25.f3d
Developpement/3D files/sensor cases/Final - Boîtier capteurs + support 2023 v53.f3d

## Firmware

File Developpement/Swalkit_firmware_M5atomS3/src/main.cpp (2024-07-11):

#include <Arduino.h>
#include <M5AtomS3.h>
#include "SwalkitBle.h"
#include "SwalkitProfile.h"
#include "SwalkitDisplay.h"
#include "sensors.h"
#include "LMA.h"

#define MAX(X,Y) ((X)>(Y)?(X):(Y))
#define MIN(X,Y) ((X)<(Y)?(X):(Y))
#define MIN3(X,Y,Z) (MIN(X,MIN(Y,Z)))


using namespace std;

// Configuration générale
String swalkit_version {"Swalkit 1.2.0"};
bool imu_enable = true;
constexpr bool usb_serial_enable = false;
constexpr bool sensors_enabled = true;
constexpr bool motors_enabled = true;
constexpr bool display_imu_data = false;

// imu
float total_acceleration;
float seuil_mouvement;
float ax, ay, az;   // accelerations
constexpr size_t gyro_data_size = 10;
float gyro_data[gyro_data_size];
size_t gyro_index;
float gyro_calibration = 0;
float gyro_threshold = 40;
bool moving = true;
unsigned long watchdog_imu_move = 5000; // 5 secondes
unsigned long last_time_moved = 0;      // secondes
float acceleration_threshold = 0.015f;   // relative to calibration

// Configuration Bluetooth
SwalkitProfile swalkitProfile;
Sensors sensors;
SwalkitBLE swalkitBLE(swalkitProfile, sensors, usb_serial_enable);
SwalkitDisplay swalkitDisplay{};
bool bluetooth_enabled = false;

// Déclarations
LMA lma;
String no_message{};

// button state
enum swalkit_btn_state
{
    on_short_pressed,
    on_long_press,
    on_long_press_released,
    idle
};
swalkit_btn_state btn_state = idle;

// tasks
void sense_and_drive_task(void *pvParameters);
void handle_button_state(void *pvParameters);

// gyro
void read_gyro_data();
float get_current_gyro();

void setup()
{
    // Initialisation du M5stack
    M5.begin(true, usb_serial_enable, true, false);
    swalkitDisplay.Init();
    swalkitDisplay.SetSwalkitState(SwalkitDisplay::SwalkitState::Initialising);
    swalkitDisplay.SetMessage(swalkit_version);
    delay(3000);
    swalkitDisplay.SetMessage(no_message);

    // default in M5atomS3 is Wire1 tu use MPU6886, but we are also using Wire on grove (pins 2 and 1)
    Wire.endTransmission();
    Wire.begin(2, 1, 100000L);

    // load stored profile
    if (!swalkitProfile.load())
    {
        swalkitDisplay.SetError("Error loading profile");
        delay(5000);
        swalkitDisplay.SetError(no_message);
    }

    delay(2000);
    if (usb_serial_enable)
        USBSerial.println("Starting...");

    if (motors_enabled) {
        // Init. de la communication I2C avec les moteurs LMA
        if (usb_serial_enable)
            USBSerial.println("Lma begin...");
        lma.begin();
    }

    if (imu_enable)
    {
        // Init. de la centrale inertielle pour la detection de mouvement
        if (usb_serial_enable)
            USBSerial.println("IMU begin...");

        swalkitDisplay.SetSwalkitState(SwalkitDisplay::SwalkitState::Calibrating);

        M5.IMU.begin();
        seuil_mouvement = 0;
        for (int i = 0; i < 10; i++)
        {
            M5.IMU.getAccel(&ax, &ay, &az);
            total_acceleration = std::sqrt(ax * ax + ay * ay + az * az);
            seuil_mouvement += total_acceleration;
            read_gyro_data();
            delay(200);
        }
        seuil_mouvement *= 0.1f;
        gyro_calibration = get_current_gyro();
        if (usb_serial_enable) {
            USBSerial.print("seuil mouvement : ");
            USBSerial.print(seuil_mouvement);
            USBSerial.print("  calibration gyro : ");
            USBSerial.println(gyro_calibration);
        }
    }


    if (sensors_enabled) {
        // Init. de la communication I2C avec les capteurs
        if (usb_serial_enable)
            USBSerial.print("sensors begin...");
        sensors.begin(false);
        if (usb_serial_enable)
            USBSerial.println("done");
    }

    if (motors_enabled) {
        // Init. de la configuration les moteurs LMA
        lma.on_off(true);
        lma.set_duty_max(UINT16_MAX);
        // lma.write(UINT16_MAX,UINT16_MAX);
    }
    
    //init lcd
    delay(200);
    swalkitDisplay.SetSwalkitState(SwalkitDisplay::SwalkitState::Ready);

    // Init. des tâches multiples paralleles
    xTaskCreatePinnedToCore(handle_button_state, "handle_button_state_task", 4096, NULL, 3, NULL, 0);
    xTaskCreatePinnedToCore(sense_and_drive_task, "sense_and_drive_task", 2048, NULL, 1, NULL, 0);
    // TODO check stack size with uxTaskGetStackHighWaterMark https://www.freertos.org/uxTaskGetStackHighWaterMark.html

    if (usb_serial_enable)
        USBSerial.println("Running...");

}

enum class SignalRange {
    Danger,
    Near,
    Far,
    Away
};

SignalRange getRangeFromDistance(int distance, int &intensity, int &pulse) {
    if (distance < swalkitProfile.dangerSignal.distance) {
        intensity = swalkitProfile.dangerSignal.intensity;
        pulse = swalkitProfile.dangerSignal.pulse;
        return SignalRange::Danger;
    }
    if (distance < swalkitProfile.nearSignal.distance) {
        intensity = swalkitProfile.nearSignal.intensity;
        pulse = swalkitProfile.nearSignal.pulse;
        return SignalRange::Near;
    }
    if (distance < swalkitProfile.farSignal.distance) {
        intensity = swalkitProfile.farSignal.intensity;
        pulse = swalkitProfile.farSignal.pulse;
        return SignalRange::Far;
    }
    intensity = 0;
    pulse = 0;
    return SignalRange::Away;
}

void sense_and_drive_task(void *pvParameters)
{
    // UBaseType_t uxHighWaterMark;
    // uxHighWaterMark = uxTaskGetStackHighWaterMark(NULL);
    // USBSerial.println(uxHighWaterMark);
    unsigned long now;
    int leftIntensity, rightIntensity, pulse;
    unsigned long last_pulsation = 0;
    bool pulsing = false;
    float gyro_value;

    while (1) {
        if (sensors_enabled) {
            sensors.read();
        }
        now = millis();
        leftIntensity = rightIntensity = 0;

        if (imu_enable)
        {
            M5.IMU.getAccel(&ax, &ay, &az);
            total_acceleration = std::sqrt(ax * ax + ay * ay + az * az) * 0.1f + total_acceleration * 0.9f;

            read_gyro_data();
            gyro_value = abs(get_current_gyro() - gyro_calibration);

            if (display_imu_data && !moving) { 
                bool bAcc = abs(total_acceleration - seuil_mouvement) > acceleration_threshold;
                bool bGyro = gyro_value > gyro_threshold;
                char buffer[64];
                *buffer = 0;
                if (bAcc) {
                    if (bGyro) {
                        sprintf(buffer, "Acc : %.3f, Gyro : %.1f", abs(total_acceleration - seuil_mouvement), gyro_value);
                    } else {
                        sprintf(buffer, "Acc : %.3f", abs(total_acceleration - seuil_mouvement));
                    }
                } else if (bGyro) {
                    sprintf(buffer, "Gyro : %.1f", gyro_value);
                }
                swalkitDisplay.SetMessage(no_message);
                if (*buffer) swalkitDisplay.SetMessage(buffer);
            }            

            if (abs(total_acceleration - seuil_mouvement) > acceleration_threshold || gyro_value > gyro_threshold) {
                moving = true;
                swalkitDisplay.SetImuState(SwalkitDisplay::IMUState::Moving);
                last_time_moved = now;
            } else if (now - last_time_moved > watchdog_imu_move) {
                swalkitDisplay.SetMessage(no_message);
                moving = false;
                swalkitDisplay.SetImuState(SwalkitDisplay::IMUState::Stopped);
            }
        }

        // for 8 sensors

        if (moving) {
            int pulseId = 0;
            int rightId = 0;
            int leftId = 0;

            int pulseTab[5] = {0, swalkitProfile.farSignal.pulse, swalkitProfile.nearSignal.pulse, swalkitProfile.dangerSignal.pulse, swalkitProfile.frontSignal.pulse};
            int sideTab[4] = {0, swalkitProfile.farSignal.intensity, swalkitProfile.nearSignal.intensity, swalkitProfile.dangerSignal.intensity};


            int front_distance = MIN3(MAX(sensors.sensor_average[2]->getAverage(), sensors.sensor_average[5]->getAverage()), sensors.sensor_average[3]->getAverage(), sensors.sensor_average[4]->getAverage());
            int right_distance = MIN3(sensors.sensor_average[0]->getAverage(), sensors.sensor_average[1]->getAverage(), sensors.sensor_average[2]->getAverage());
            int left_distance = MIN3(sensors.sensor_average[5]->getAverage(), sensors.sensor_average[6]->getAverage(), sensors.sensor_average[7]->getAverage());

            // center
            if (front_distance < swalkitProfile.frontSignal.distance) {
                leftIntensity = rightIntensity = swalkitProfile.frontSignal.intensity;
                pulse = swalkitProfile.frontSignal.pulse;
            } else {
                int rightPulse;
                SignalRange leftRange = getRangeFromDistance(left_distance, leftIntensity, pulse);
                SignalRange rightRange = getRangeFromDistance(right_distance, rightIntensity, rightPulse);
                if (leftRange > rightRange) {   // keep only closest range if both are different
                    leftIntensity = 0;
                    pulse = rightPulse;
                } else if (rightRange > leftRange) {
                    rightIntensity = 0;
                }
            }

            if (pulse != 0) {   // manage pulse if set
                if (pulsing) {
                    leftIntensity = rightIntensity = 0;
                }
                if ((now - last_pulsation) > pulse) {
                    pulsing = !pulsing;
                    last_pulsation = now;
                }
            }
        }

        if (motors_enabled) {
            uint16_t write_result = lma.write(rightIntensity * (UINT16_MAX / 100), leftIntensity * (UINT16_MAX / 100));
            if (write_result != 0) {
                swalkitDisplay.SetError("LMA Write error " + String(write_result));
            } else {
                swalkitDisplay.SetError(no_message);
            }
            swalkitDisplay.SetMotorsState(
                leftIntensity > 0 ? SwalkitDisplay::MotorState::Running : SwalkitDisplay::MotorState::Stopped,
                rightIntensity > 0 ? SwalkitDisplay::MotorState::Running : SwalkitDisplay::MotorState::Stopped
            );
        }

        // uxHighWaterMark = uxTaskGetStackHighWaterMark(NULL);
        // USBSerial.println(uxHighWaterMark);
    }
}


void loop()
{
    M5.update(); // Btn read

    if (M5.Btn.wasReleased())
    {
        if (btn_state == on_long_press)
            btn_state = on_long_press_released;
        else
            btn_state = on_short_pressed;
    }

    if (M5.Btn.pressedFor(500))
    {
        btn_state = on_long_press;
    }
}
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

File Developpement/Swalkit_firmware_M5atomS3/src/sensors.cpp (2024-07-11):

#include "sensors.h"

const unsigned char RA_SIZE = 4;  //RunningAverage size for the sensors
const unsigned int SENSOR_MAX_VALUE =  80;

#define VL53L0X_ADDRESS_DEFAULT 0b0101001

// Configuration des HUB i2c intelligents
uint8_t TCA9548A_ADDRESS_1 = 0x73;
uint8_t TCA9548A_ADDRESS_2 = 0x70;

unsigned char HUB_1_I2C_SENSORS_CHANNELS [4]= {
    TCA_CHANNEL_0,
    TCA_CHANNEL_1,
    TCA_CHANNEL_2,
    TCA_CHANNEL_3,
};
unsigned char HUB_2_I2C_SENSORS_CHANNELS [4]= {
    TCA_CHANNEL_3,
    TCA_CHANNEL_2,
    TCA_CHANNEL_1,
    TCA_CHANNEL_0,
};
unsigned char HUB_1_SENSORS_ADDRS [4]= {
    0x2A, 0x2B, 0x2C, 0x2D};
unsigned char HUB_2_SENSORS_ADDRS [4]= {
    0x2F, 0x2E, 0x29, 0x30};

Sensors::Sensors() : _debug(false){
      for (int i = 0; i < NUMBER_OF_SENSORS; i++) {
        sensor_average[i] = new RunningAverage<int>(RA_SIZE);
        sensor_average[i]->fillValue(80,RA_SIZE);
    }

    for (int i = 0; i < NUMBER_OF_SENSORS; i ++) {
        sensor[i] = new Adafruit_VL53L0X();  
    }
}

void Sensors::begin(bool debug)
{
    _debug = debug;
    TCA_HUB_1.begin(Wire, TCA9548A_ADDRESS_1); // Start first Multiplexer
    TCA_HUB_1.closeAll();
    TCA_HUB_2.begin(Wire, TCA9548A_ADDRESS_2); // Start second Multiplexer
    TCA_HUB_2.closeAll();
    for (int i = 0; i < NUMBER_OF_SENSORS/2; i ++) {
      TCA_HUB_1.closeAll();
      TCA_HUB_1.openChannel(HUB_1_I2C_SENSORS_CHANNELS[i]);

      Wire.beginTransmission(VL53L0X_ADDRESS_DEFAULT);
      byte error = Wire.endTransmission();

      if(error == 0)
      {
          sensor[i]->begin();
          sensor[i]->setAddress(HUB_1_SENSORS_ADDRS[i]);
      }
      else //RESET of the atoms3 case, sensors already init with new address
      {
          sensor[i]->begin(HUB_1_SENSORS_ADDRS[i]);
      }
      sensor[i]->startRangeContinuous(20);
    }   
    TCA_HUB_1.closeAll();

    TCA_HUB_2.begin(Wire, TCA9548A_ADDRESS_2); // Start second Multiplexer
  for (int i = 0; i < NUMBER_OF_SENSORS/2; i ++) {
      TCA_HUB_2.closeAll();
      TCA_HUB_2.openChannel(HUB_2_I2C_SENSORS_CHANNELS[i]);

      Wire.beginTransmission(VL53L0X_ADDRESS_DEFAULT);
      byte error = Wire.endTransmission();
      if(error == 0)
      {
          sensor[i+ NUMBER_OF_SENSORS/2]->begin();
          sensor[i+ NUMBER_OF_SENSORS/2]->setAddress(HUB_2_SENSORS_ADDRS[i]);
      }
      else //RESET of the atoms3 case, sensors already init with new address
      {
          sensor[i+ NUMBER_OF_SENSORS/2]->begin(HUB_2_SENSORS_ADDRS[i]);
          
      }
      sensor[i+ NUMBER_OF_SENSORS/2]->startRangeContinuous(20);
    }      

    TCA_HUB_1.openAll();
    TCA_HUB_2.openAll();
}

void Sensors::read()
{
    VL53L0X_RangingMeasurementData_t m;
    for(int i = 0; i < NUMBER_OF_SENSORS; i++)
    {
        if(sensor[i]->isRangeComplete()){
            sensor[i]->getRangingMeasurement(&m);
            uint16_t measure = m.RangeMilliMeter;
            if(_debug) USBSerial.print(i);
            if(_debug) USBSerial.print("...");
            if(_debug) USBSerial.print(measure);
            if(_debug) USBSerial.print("...");
            uint8_t status = sensor[i]->readRangeStatus();
            bool measureFailed = (measure == 0 && status != 0) || status == 1 || status == 2 || status == 7 || sensor[i]->timeoutOccurred();

            if (!measureFailed) {  // phase failures have incorrect data

                if(_debug) USBSerial.println("OK");
                //if(measure == 0) measure = SENSOR_MAX_VALUE;
                sensor_average[i]->addValue(measure<SENSOR_MAX_VALUE*10?
                                measure/10 :
                                SENSOR_MAX_VALUE);
            } else {
                if(_debug) USBSerial.println("NOK");
                sensor_average[i]->addValue(SENSOR_MAX_VALUE);
            } 
        }
    } 
}

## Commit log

2022-03-10 update dev files
    [LMA Motor Case.f3d, Sensor case - support.f3d, bottomLeftSensorBox.stl, bottomRightSensorBox.stl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]
2022-03-15 clean folder names, use Swalkit bin to upload on M5stack
    [bottomLeftSensorBox.stl, bottomRightSensorBox.stl, centralUnitBottom.stl, centralUnitTop.stl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]
2023-10-05 first commit of Android app rewriting. Basic bluetooth features (no communication yet) and first version of motors screen
2023-11-27 it seems long device name may cause problems. seems to fix a problem we encountered...
2023-11-29 fix sensors plantage
2023-11-29 add logic between sensors and motors
2023-11-29 changed range of values for motor distances. cleaned up some code
2023-12-20 add new 3d
    [Boitier capteurs_Final - Boîtier capteurs + support 2023 v36_BoîtierCapteurs_L.stl, Boitier capteurs_Final - Boîtier capteurs + support 2023 v36_BoîtierCapteur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]
2024-01-08 update 3d files
    [Boitier capteurs_Final - Boîtier capteurs + support 2023 v36_BoîtierCapteurs_L.stl, Boitier capteurs_Final - Boîtier capteurs + support 2023 v36_BoîtierCapteur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]
2024-01-26 correction de francais
2024-02-13 fix readme table des matières and fix developpement folder
    [BlocMoteur(sans_supports)(miroir).2024.02.12.001.stl, BlocMoteur(sans_supports).2024.02.12.001.stl, BoitierElec.2024.02.12.001.stl, BoîtierCapteurs_Droite.2024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]
2024-02-14 update stl files
    [BoitierElec.stl, BoîtierCapteurs_L.stl, BoîtierCapteurs_R.stl, CouvercleBoitierElec.stl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]
2024-02-20 fixed a typo. Improved rendering of screw list
2024-02-22 fix sensors read slow
2024-03-04 VL53L0 changed to continuous ranging, Refactored logic behind pulses from sensors
2024-03-11 fixed some display bugs. made sensor task a bit clearer (to be tested)
2024-03-25 smoothed gyro value. Using calibration for inital gyro value. motors and sensors may now be disabled by code (for testing M5Stack alone)
2024-03-25 DrawText now handles \n characters. Fixed text centering. Reactivated motors and sensors.
2024-03-27 update dev 3d files
    [Final - Boîte Élec 2023 v23.f3d, Final - Boîtier capteurs + support 2023 v53.f3d, Final - Motor Case Clean Swalkit v25.f3d, LMA Motor Case.f3d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]
2024-05-27 Display now takes String instead of char*. Added Front circles to show motor commands. LMA write now returns an error code. Displaying an error message if LMA write fails.
2024-07-11 Sensor status taken into account, Gyro max value changed to 40, HBridge firmware updated with working 16 bit speed
